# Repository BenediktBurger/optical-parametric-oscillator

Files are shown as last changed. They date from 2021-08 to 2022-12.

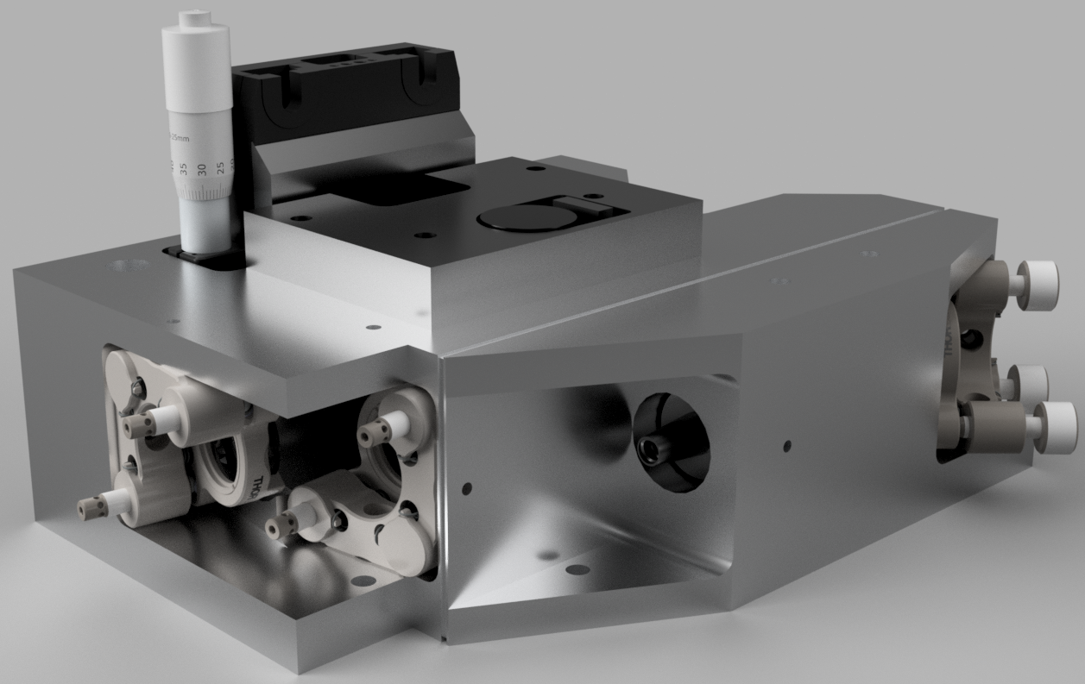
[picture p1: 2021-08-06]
images/CavityBlockSeitlich.png

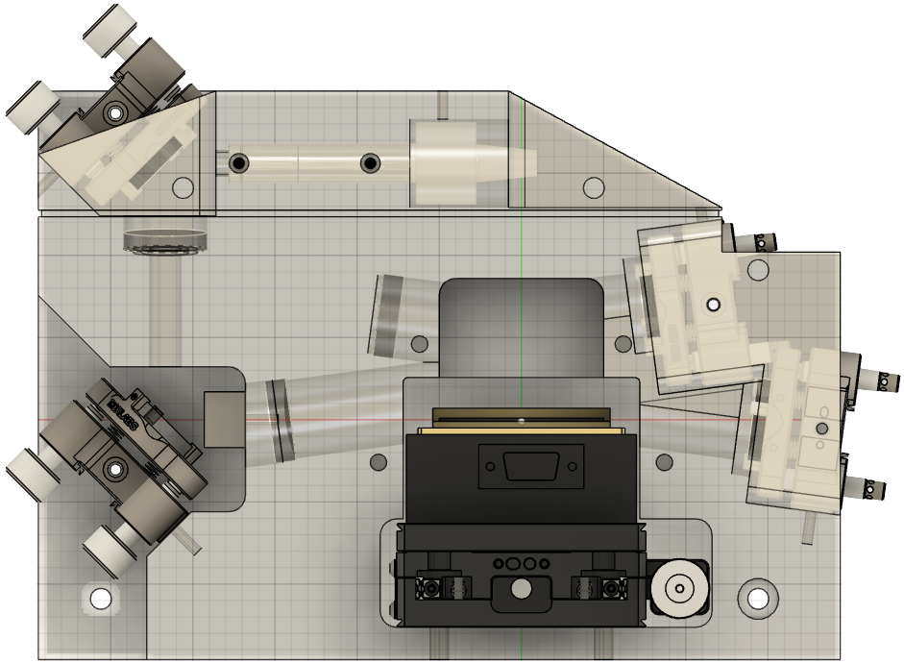
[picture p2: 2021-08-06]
drawings/OPO-Block-Oben2.png

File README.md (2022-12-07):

# Optical Parametric Oscillator

Open source hardware for a continuous wave optical parametric oscillator (OPO) in the mid-infrared regime.



## History

We needed a narrowband, tunable, continuous wave light source for coherent radiation at 606 nm. The result is this optical parametric oscillator with intra-cavity sum frequency generation, similar to a special version of the Aculight Argos 2400 laser system previously sold by Lockheed Martin. This is described in *Tunable, continuous-wave optical parametric oscillator with more than 1W output power in the orange visible spectrum* by S. Mieth et al. [DOI10.1364/OE.22.011182](https://www.osapublishing.org/oe/abstract.cfm?uri=oe-22-9-11182).

The design works for mid-infrared laser light as well, if the sum frequency part is left out. In fact, we use a second model with different mirror coatings and crystal for light at 2550 nm.

## Design Overview

The optical parametric oscillator consists in a bow-tie cavity (two concave mirrors with curvature radius of 100 mm and two planar mirrors) and a periodically poled lithium niobate crystal.

A pump laser at 1064 nm, focused into the center of the crystal, provides power for the difference frequency generation. The cavity is resonant (by mirror design) for one frequency (the *signal*) such that this frequency is amplified and the difference frequency (*idler*) is generated and emitted (see *singly resonant optical parametric oscillator*).

An etalon in the cavity (in the second focus) allows longitudinal mode selection for the signal wave.

## Folder Contents

- *designs* contains 3D designs.
- *drawings* contains some corresponding technical drawings.
- *images* contains some images and schematics of the design.
- *documentation* contains documentation of the setup.

## Construction

-The pump laser is a fiber laser by *IPG Photonics* (YAR-15K) with up to 15 W at 1064 nm. Its fiber tip contains a collimation unit (called *collimator*) with an additional clamp (made by Aculight) in order to mount it repeatedly with the same polarisation.
- Two highly reflective mirrors (1 inch diameter), mounted in *Thorlabs Polaris K1F* allow the pump beam to be adjusted.
- This collimator is mounted into the *OPO-Block* (see 3D file in *designs*) with a horizontal polarisation.
- A 0.5 inch lens with 62.9 mm focal length (*Newport KPX052AR.33*) focusses the pump power into the nonlinear crystal. It is mounted with the *Linsenhalter* (in designs).
- The nonlinear crystal is made of magnesium oxide doped (5%) lithium niobate with a periodic poling for *quasi phase matching*. A fanout structure of the poling period allows tuning via vertical translation. Use [SNLO](https://as-photonics.com/products/snlo/) for calculating the poling period. *HC Photonics* is capable of producing this crystal.
- The crystal is mounted in a heating oven (*HC Photonics TC038D*) for temperature controlling. For a python API controlling the oven temperature see [pymeasure](https://pymeasure.readthedocs.io).
- The oven is mounted to the OPO-Block via a translation stage (*Thorlabs XR25P_M*) and *Ofen-Adapterplatte* (in designs)
- Four specially coated 25mm mirrors (Anti-reflection for 1064 and the idler on both sides. Anti-reflection coating is for the signal on the outside and high-reflection on the inside), two mirrors with concave curvature of 100 mm (next to the oven) and two planar ones, form the cavity. Laseroptik made them in our case. Most important is the high reflectivity for the signal.
- One mirror is glued into the OPO-Block, one is mounted with a SM1 ring from Thorlabs and the other two (on the output side of the Block) are mounted with *Thorlabs Polaris K25F4_M* in order to adjust the cavity.
- Finally the Etalon is glued to a comercially available galvanometer (for Lasershows) and mounted to the lid *Deckel LwG* (in designs), which in turn is mounted on top of the OPO-Block to provide radiation blocking and reduce dust entering the cavity.
- For the setup and adjustments refer the files in *documentation*.

## Disclaimer

These files are provided by the copyright holders and contributors "as is" and any express or implied warranties, including, but not limited to, the implied warranties of merchantability and fitness for a particular purpose are disclaimened. In no event shall the copyright owner or contributors be liable for any direct, indicrect, insidental, special, exemplary, or consequential damages however caused and on any theory of liability, wheter in contract, strict liability, ort tort (including negligence or otherwise) arising in any way out of the use of these files, even if advised of the possibility of such damage.

This is a class IV laser system. Adhere to local regulations and apply necessary safetey measurements.

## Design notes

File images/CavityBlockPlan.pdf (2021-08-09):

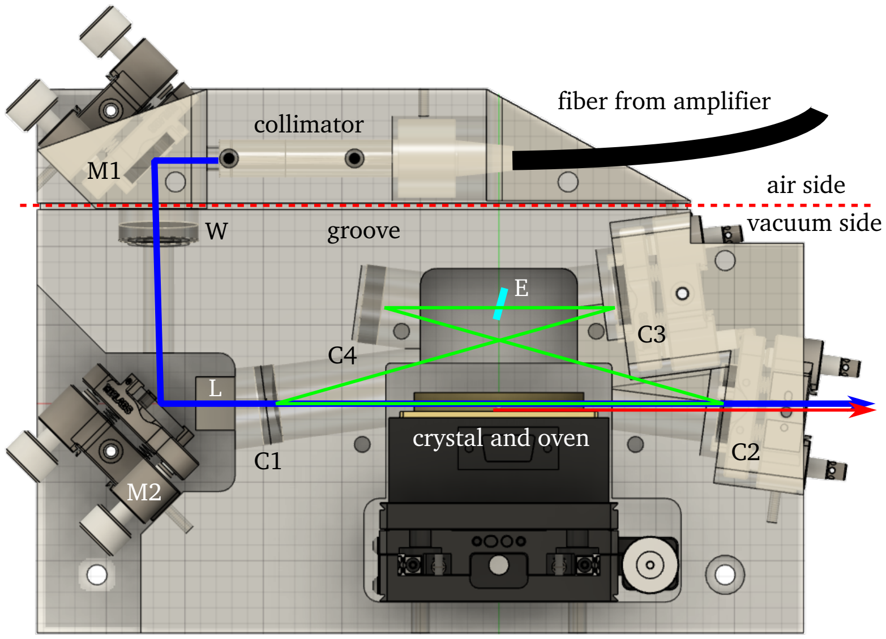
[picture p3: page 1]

collimator
M1

M2

W

L

C1 | C2

C3
C4

crystal and oven

groove

air side
vacuum side

E

fiber from amplifier

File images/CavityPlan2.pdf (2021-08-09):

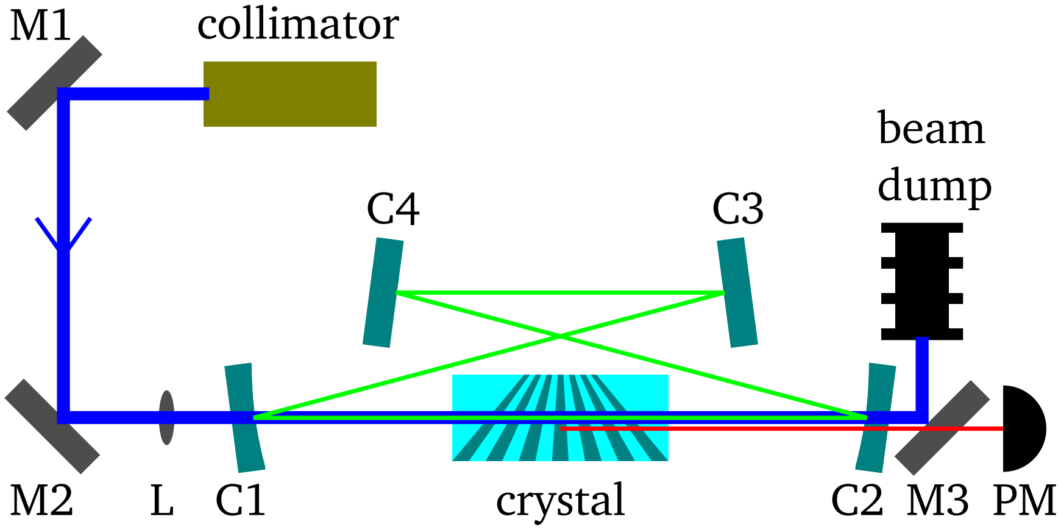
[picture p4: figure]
collimator; beam dump; crystal

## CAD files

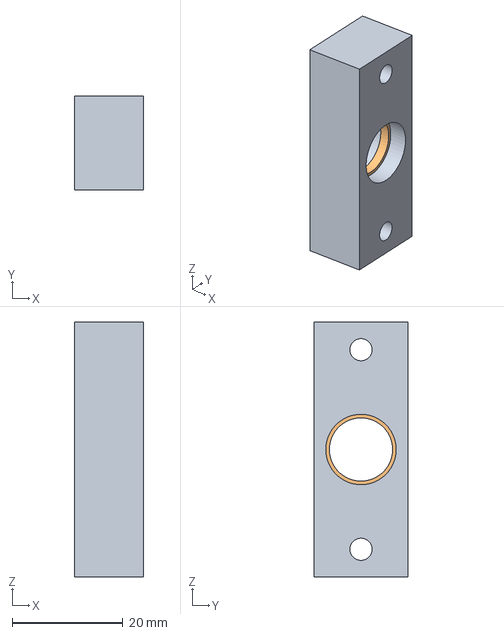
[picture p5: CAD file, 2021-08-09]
designs/Linsenhalter.step
12.5 x 17.0 x 46.0 mm

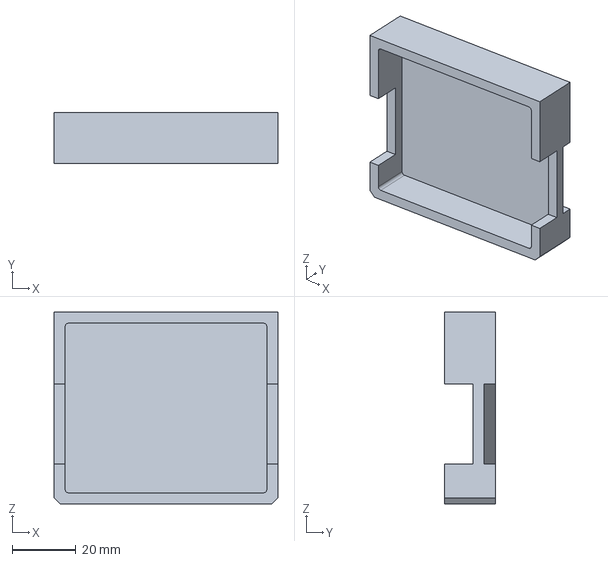
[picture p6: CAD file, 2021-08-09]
designs/Ofen-Deckel.step
70.0 x 16.0 x 60.0 mm

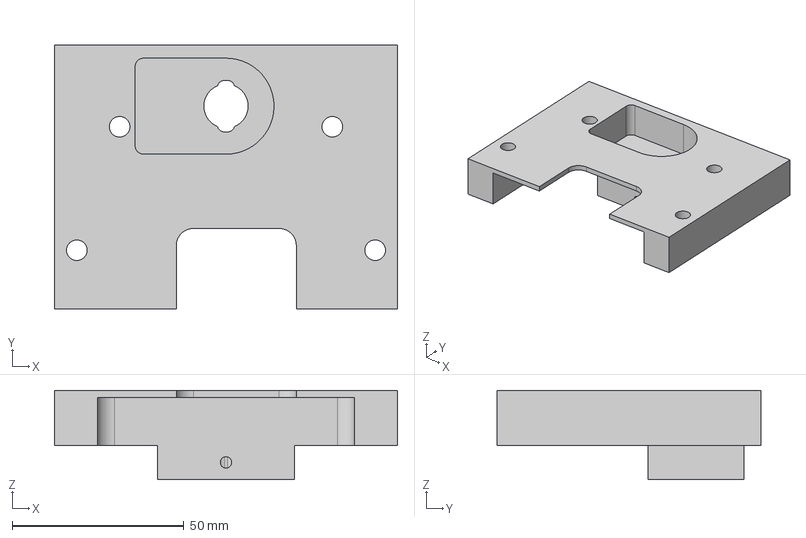
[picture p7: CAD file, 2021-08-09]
designs/Deckel LwG.step
100.0 x 77.0 x 26.0 mm

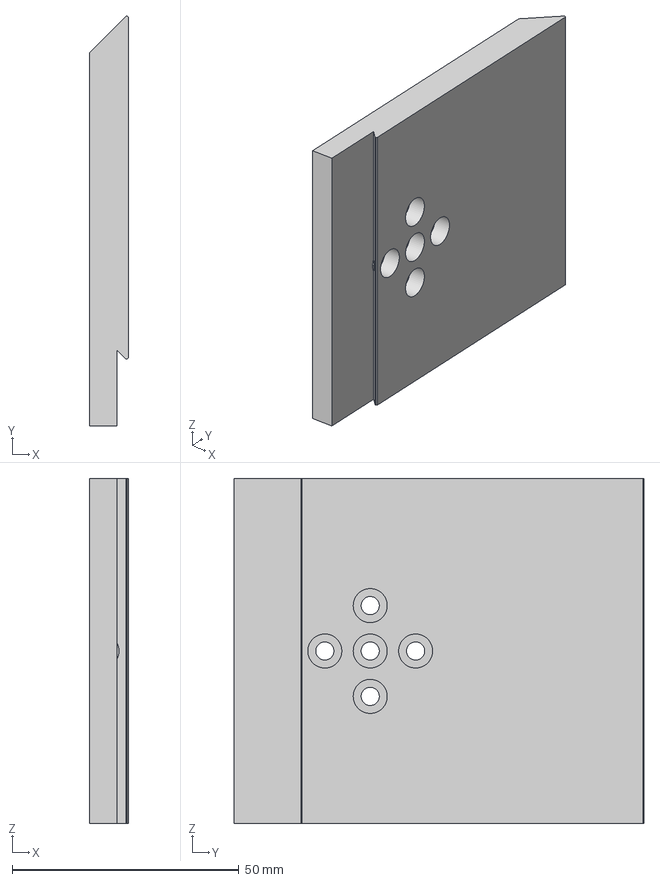
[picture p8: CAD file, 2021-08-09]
designs/Ofen-Adapterplatte.step
8.50 x 90.3 x 76.0 mm

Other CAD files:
designs/Deckel LwG.f3d
designs/OPO-Block.f3d
designs/Ofen-Adapterplatte.f3d

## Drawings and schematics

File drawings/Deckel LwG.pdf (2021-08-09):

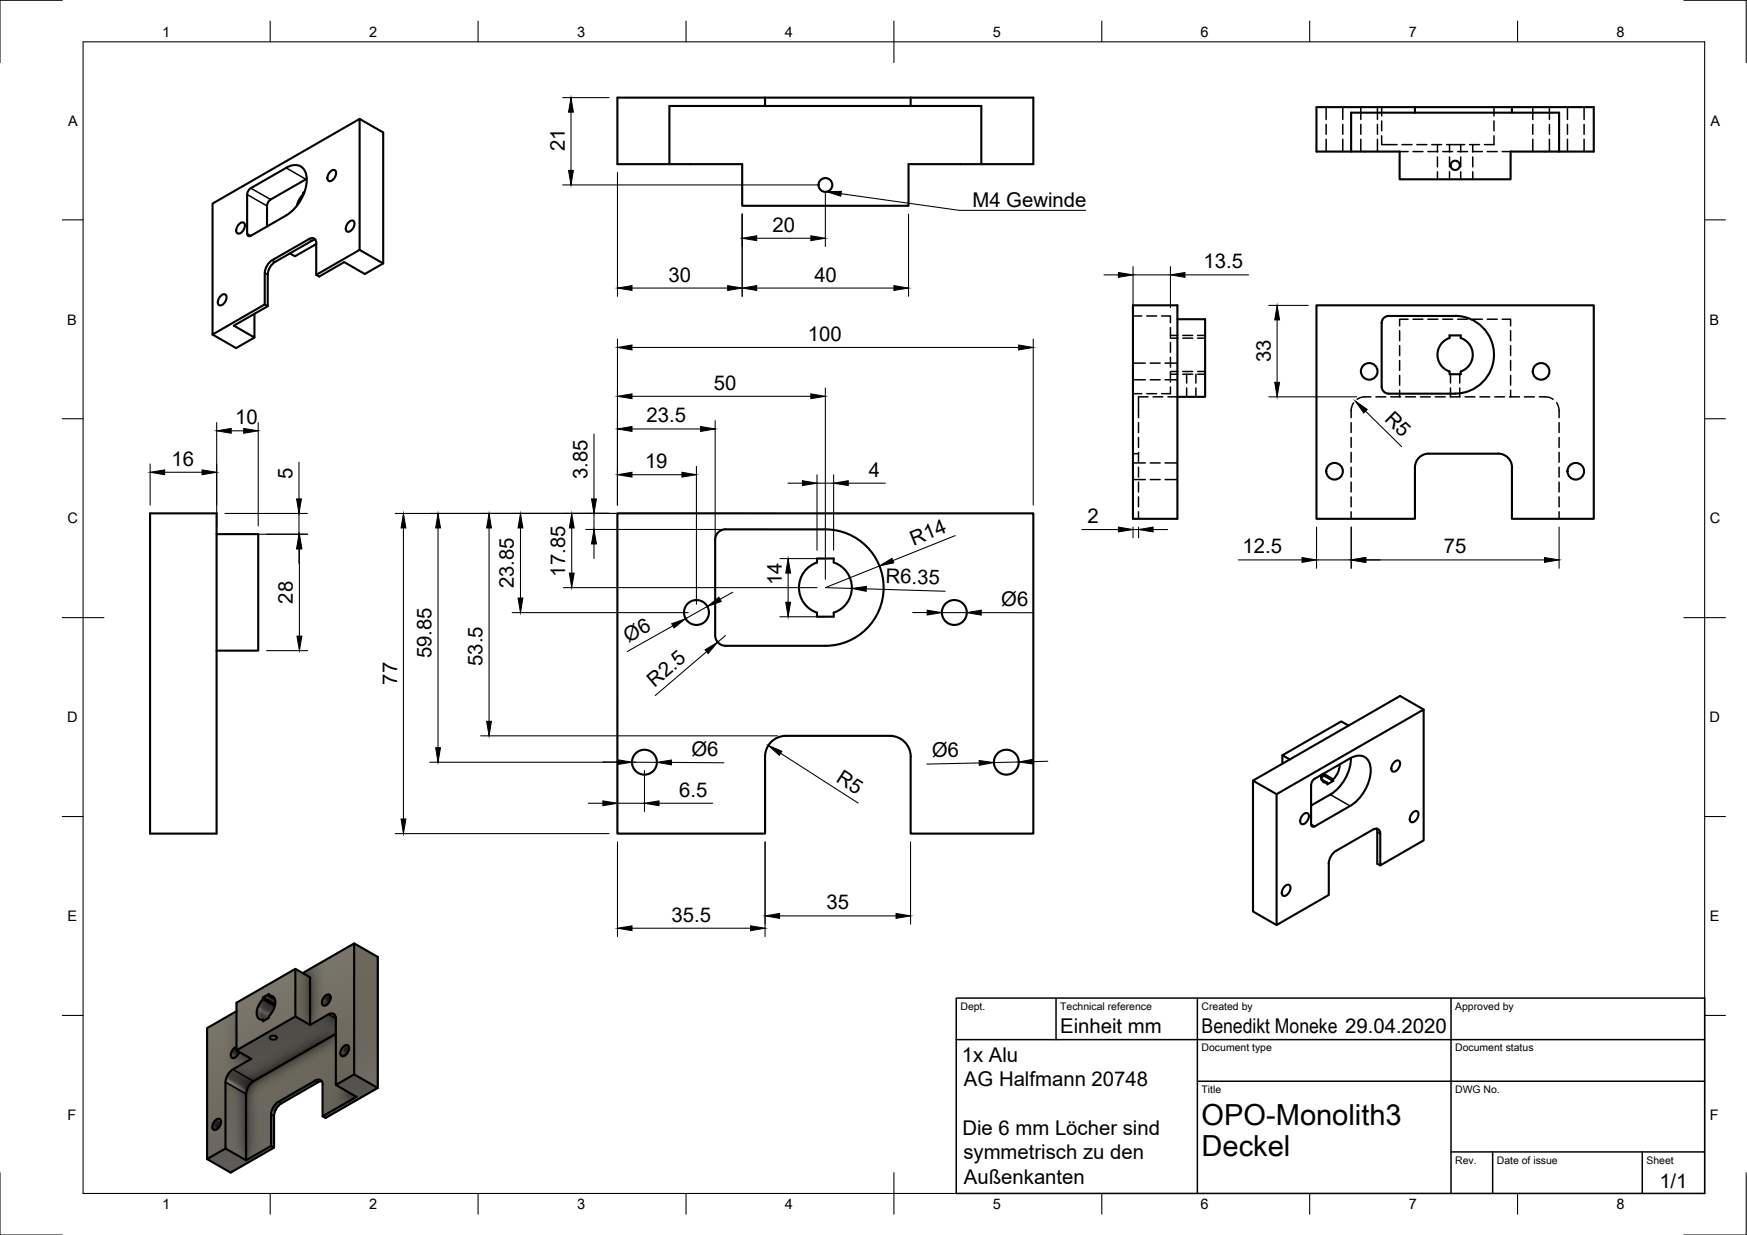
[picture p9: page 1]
M4 Gewinde 53.5

Dept. | Technical reference Einheit mm | Created by Benedikt Moneke 29.04.2020 | Approved by

1x Alu AG Halfmann 20748 Die 6 mm Löcher sind symmetrisch zu den Außenkanten | | Document type | Document status

Title OPO-Monolith3 Deckel | DWG No.

Rev. | Date of issue | Sheet 1/1

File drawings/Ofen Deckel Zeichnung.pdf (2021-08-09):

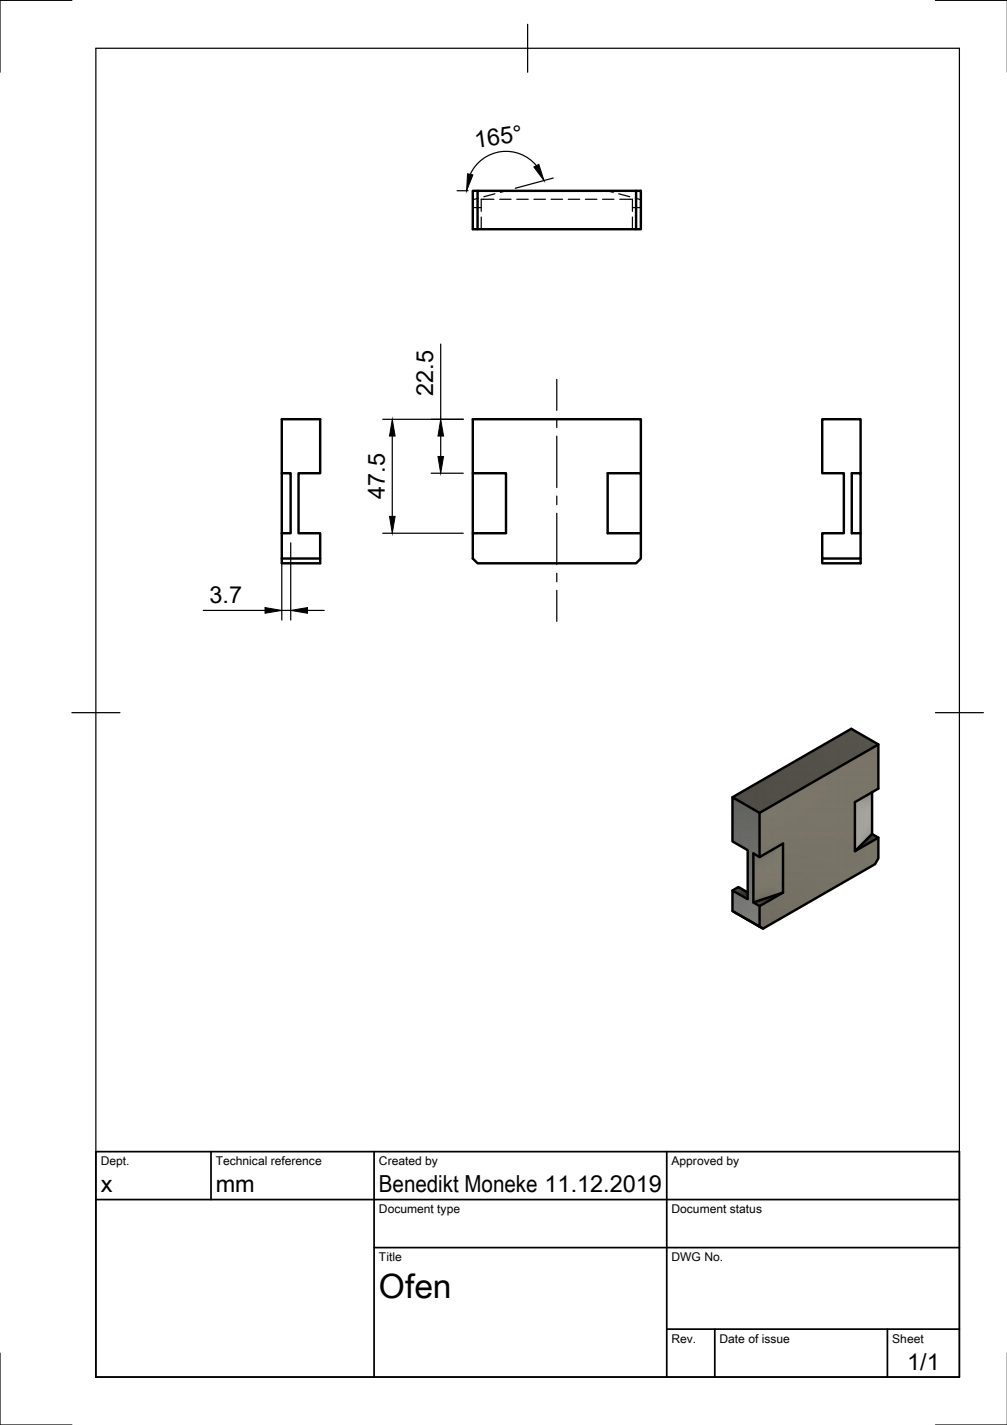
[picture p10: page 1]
Benedikt Moneke 22.5 47.5

Dept. | Technical reference | Created by 11.12.2019 | Approved by

Document type | Document status

Title Ofen | DWG No.

Rev. | Date of issue | Sheet 1/1

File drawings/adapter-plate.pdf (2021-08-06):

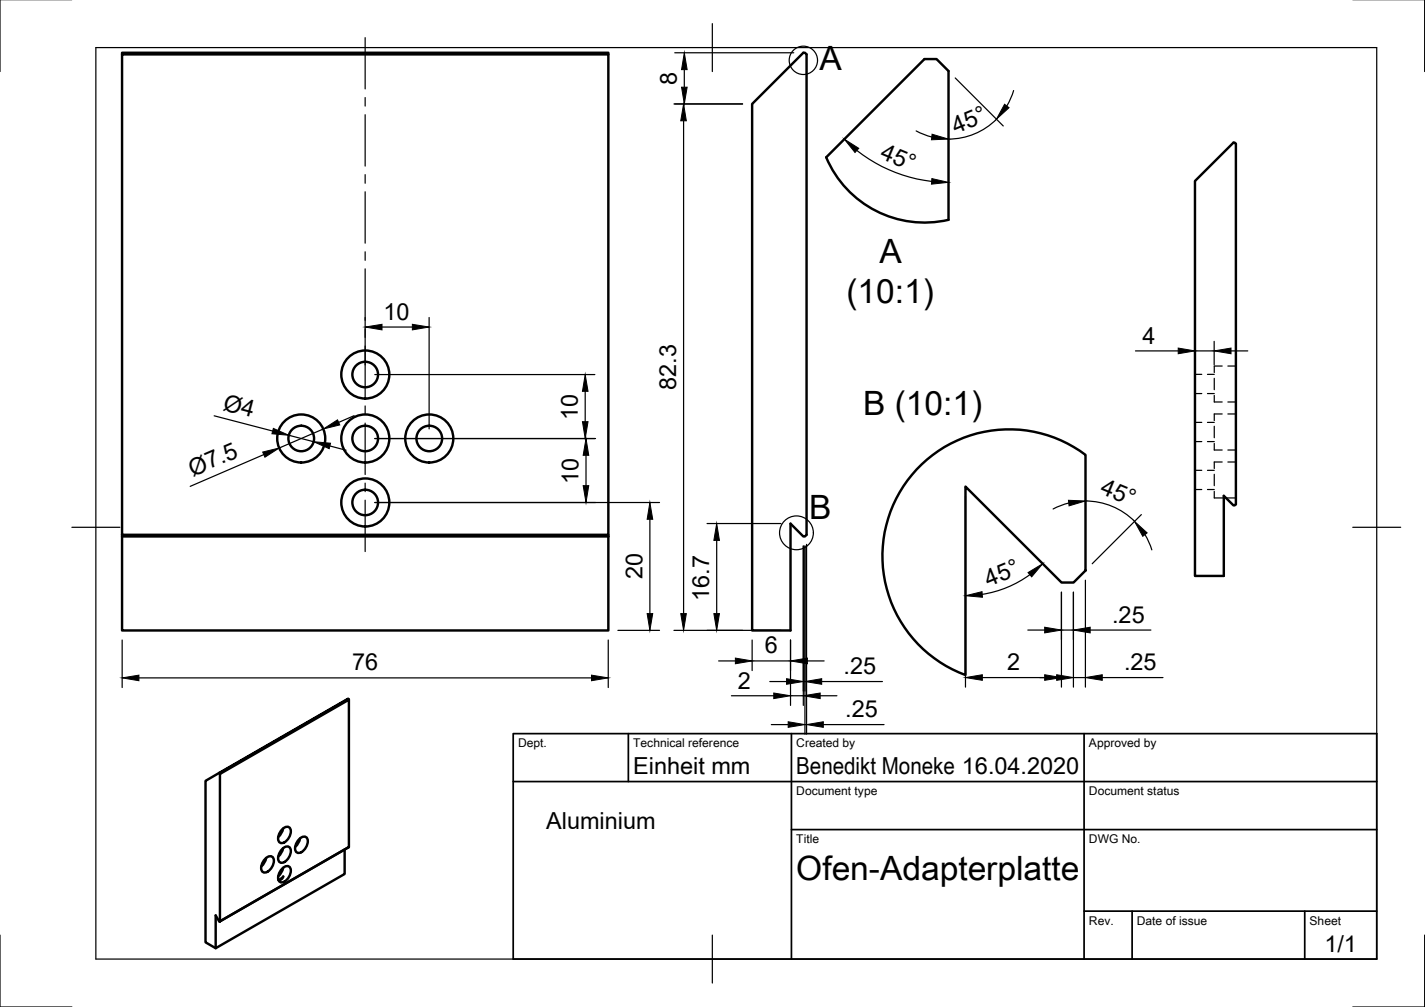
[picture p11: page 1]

Dept. | Technical reference Einheit mm | Created by Benedikt Moneke 16.04.2020 | Approved by

Aluminium | | Document type | Document status

Title Ofen-Adapterplatte | DWG No.

Rev. | Date of issue | Sheet 1/1

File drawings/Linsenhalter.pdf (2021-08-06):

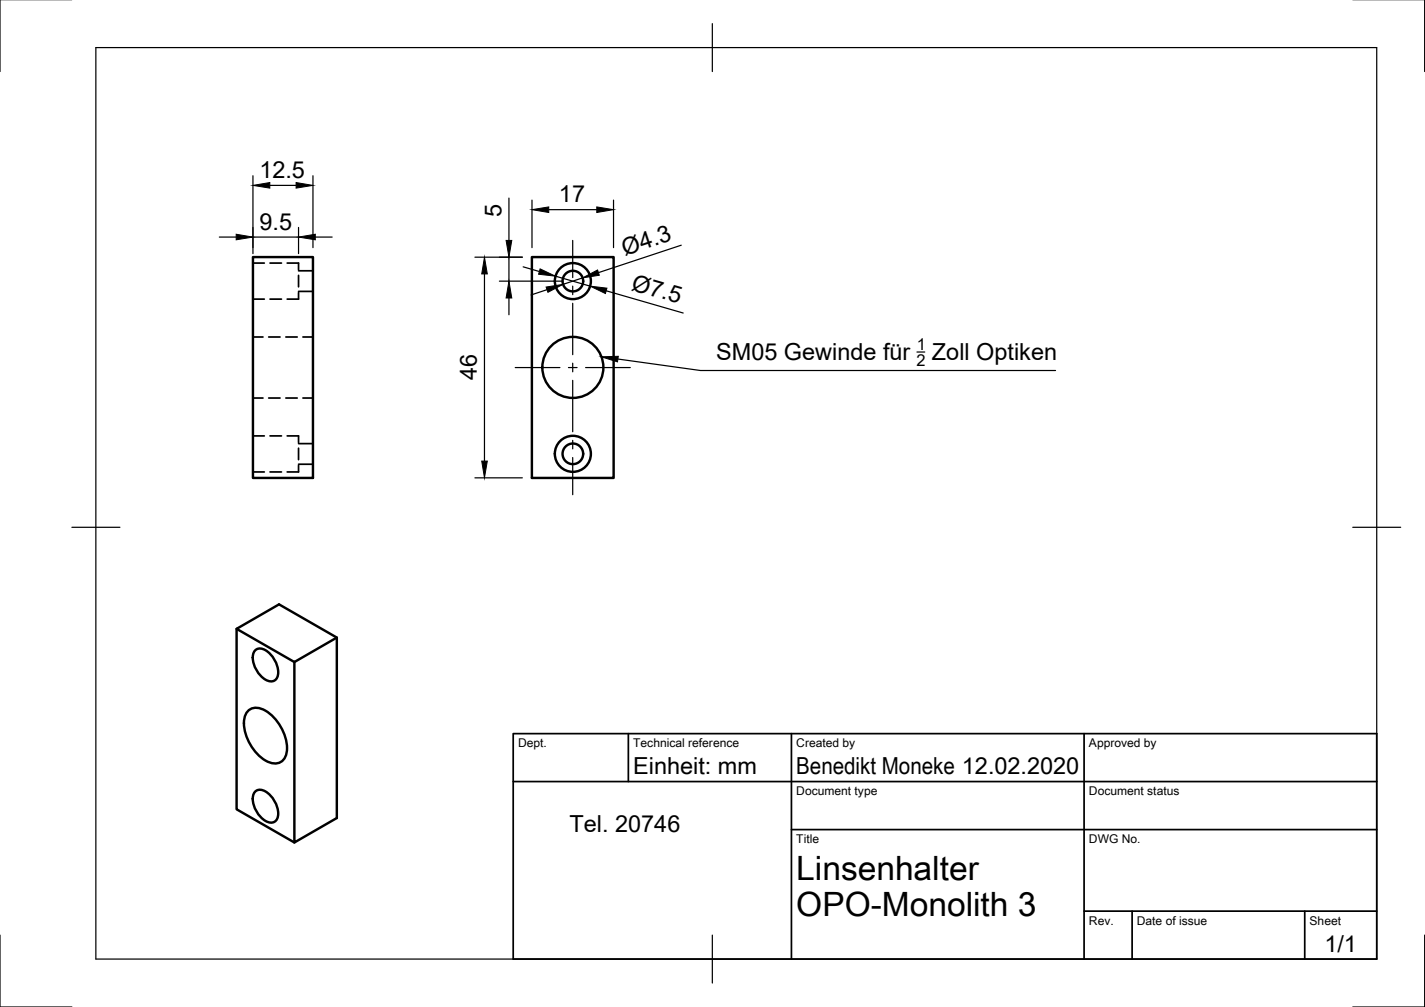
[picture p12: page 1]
SM05 Gewinde für 1; Zoll Optiken

Dept. | Technical reference Einheit: mm | Created by Benedikt Moneke 12.02.2020 | Approved by

Tel. 20746 | | Document type | Document status

Title Linsenhalter OPO-Monolith 3 | DWG No.

Rev. | Date of issue | Sheet 1/1

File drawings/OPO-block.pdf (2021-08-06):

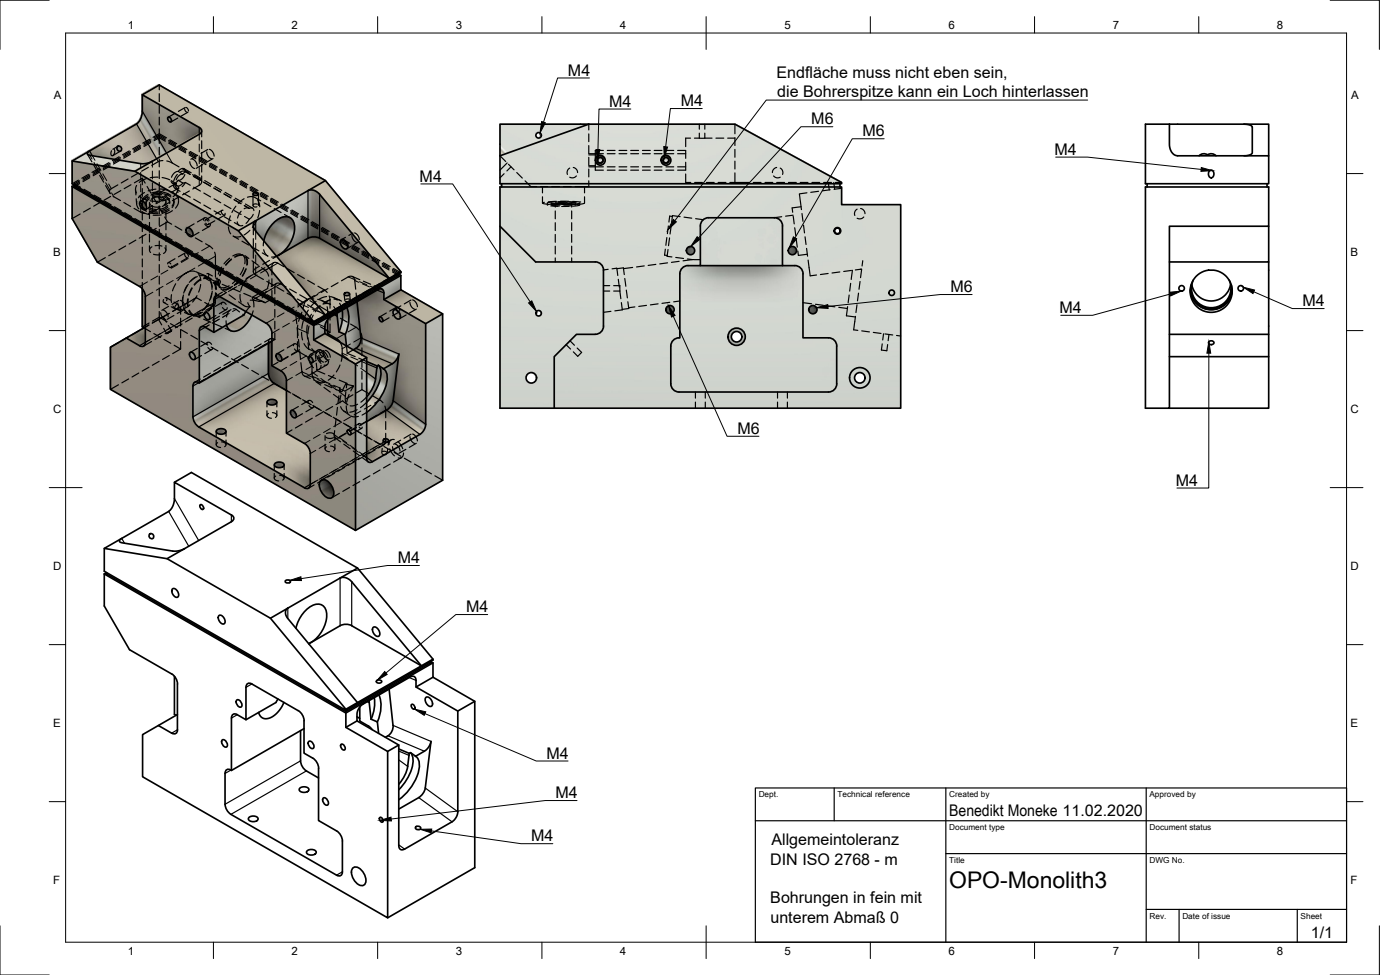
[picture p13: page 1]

Endfläche muss nicht eben sein,
die Bohrerspitze kann ein Loch hinterlassen

Dept. | Technical reference | Created by Benedikt Moneke 11.02.2020 | Approved by

Allgemeintoleranz DIN ISO 2768 - m Bohrungen in fein mit unterem Abmaß 0 | | Document type | Document status

Title OPO-Monolith3 | DWG No.

Rev. | Date of issue | Sheet 1/1

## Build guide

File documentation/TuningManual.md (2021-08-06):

# Anleitung zur Justage eines OPOs

Die Informationen dieser Anleitung wurden aus der Justage des OPOs für [Experiment] META Aufbau neuer OPO und bei [Experiment] META MOT606 Conversion von 795 nm zu 606 nm gewonnen und nutzen die Tipps, die von verschiedenen Anwendern des Moduls Aculight Argus von Lockheed Martin gegeben wurden.

## Anwendungsbereich

Das Wissen wurde an OPOs gewonnen, die infrarot (1064 nm) gepumpt werden und deren Signalstrahlung (kürzere Wellenlänge der Differenzfrequenzgeneration) in einem Resonator um den periodisch gepolten nichtlinearen Kristall (PPLN) umläuft. Der Resonator ist in Doppel-Z-Konfiguration aufgebaut. Die Spiegel direkt am Kristall sind gekrümmt, die anderen planar.

Für die weiteren Hinweise gilt folgende Nomenklatur:

- *Einkoppler* ist der gekrümmte Kavitäts-Spiegel, durch den die Pumpe in die Kavität eingekoppelt wird.
- *Auskoppler* ist der gekrümmte Kavitäts-Spiegel, durch den Pumpe, Idler und sichtbares Licht ausgekoppelt wird.
- *Gegeneinkoppler* ist der planare Kavitäts-Spiegel, der gegenüber dem Einkoppler und zu diesem parallel steht.
- *Gegenauskoppler* ist der planare Kavitäts-Spiegel, der gegenüber dem Auskoppler und zu diesem parallel steht.

## 1. Aufbau und Vorjustage

Zu Beginn müssen die Spiegel an ihren Plätzen und in richtiger Ausrichtung aufgebaut werden, wozu eine Papierskizze helfen kann. Zur genaueren Ausrichtung kann ein sichtbarer Laserstrahl, zum Beispiel ein roter Diodenlaser oder ein grüner Laserpointer verwendet werden, solange das Licht einen Umlauf im Resonator machen kann. Dieser temporäre Laserstrahl sollte zwei Spiegel zentral treffen und die Spiegel so justiert werden, dass der Strahl einmal umläuft. Dazu ist es hilfreich, wenn der Kristall noch nicht verbaut ist. Auch kann man die Strahlen erst anhand der angefertigten Skizze ausrichten.

Der Kristall ist so verbaut, dass eine Höhenänderung die Polungsperiode ändert und er nur 0,5-1 mm breit ist.

Zur leichteren Justage sollte kein Etalon im Resonator eingebaut sein.

## 2. Justage der Pumpe

Die Pumpe sollte anfangs, mit schwacher Leistung, zentral auf die beiden gegenüberliegenden Spiegel (Einkoppler, Auskoppler) ausgerichtet werden, anschließend der Kristall eingebaut und die Pumpe so horizontal justiert werden, dass sie vorne zentral den Kristall trifft und hinten zentral verlässt, dazu ist eine Strahlkamera hilfreich, oder mit einer Wandlerkarte. Dadurch ist der Strahl in der horizontalen durch Ort und Winkel justiert.

In den verwendeten Kristallen enstand ab 0,5 W Pumpleistung die Frequenzverdoppelte der Pumpleistung, diese Frequenzverdoppelte (bei 532 nm, ab jetzt grünes Licht genannt) ist hilfreich zur weiteren Justage.

Der vertikale Ort ist relativ unwichtig, da er duch die Kristallverschiebung eingestellt wird. Der Winkel ist wichtig, um möglichst eine konstante Polungsperiode für die Pumpe zu haben. Der Winkel wird über den Spiegel der Pumpstrahlung eingestellt, der am nächsten der Kavität steht. Die verwendeten Kristalle hatten eine Beschichtung, die einen signifikanten Anteil grünen Lichtes reflektiert, sodass der Kristall wie ein Etalon wirkt und bei vertikaler Verkippung eine vertikale Reihe von Punkten erzeugt. Ziel ist es, diese Punkte zu überlagern, um ungefähr senkrecht auf den Kristall zu treffen. Umso näher man diesem Punkt kommt, umso heller wird das grüne Licht und der senkrechte Treffer zeigt sich durch eine markante Intensitätsspitze. Zwischen dem Ort maximaler Intensität und dem Ort bester Überlagerung liegt der Ort, der später die höchste Leistung bringt. Am besten auf maximale Intensität einstellen und leicht in Richtung einen Punkt gehen. Es empfiehlt sich diese vertikalen Punkte auf einem reflektierten Strahl anzuschauen, an dem die Pumpe nicht mehr vorhanden ist. Eine sinnvolle Einstellung sind 1-3 W, um genug grünes Licht zu haben.

Mit senkrechtem Treffer auf die Kristalloberfläche und guter Strahlführung durch den Kristall ist die Pumpe fertig justiert, sofern die Kavität justierbar ist.

## 3. Grobjustage der Kavität

Es empfiehlt sich, die Spiegel, die von der Pumpe durchlaufen werden (zumindest den Einkoppler), nicht anzufassen, um die Pumpe während der Justage nicht abzulenken und den Kristall zu beschädigen. Justiert wird mit Hilfe der anderen Spiegel.

Auch hier wird grünes Licht verwendet, aber nur das Licht, das vorne aus dem Kristall austritt und nicht dasjenige, das an der Austrittsseite reflektiert wird und rückwärtig umläuft. Man beobachtet das grüne Licht, das aus einem oder mehreren Spiegeln austritt an verschiedenen Orten: Nahe am Spiegel und weiter entfernt, ca 15-30 cm. Nun versucht man das Licht, das direkt aus dem Spiegel austritt mit demjenigen zu überlagern, das nach einem weiteren Umlauf erst austritt. Mit einem ersten Spiegel (Auskoppler oder Gegenauskoppler) wird auf den nahen Ort justiert, mit einem späteren Spiegel (zum Beispiel Gegeneinkoppler) wird auf den fernen Ort justiert.

Um zu erkennen, welches Licht einen weiteren Umlauf hinter sich hat, muss man den Resonator an einem Ort blocken, wo nur Licht lang kommt, das mindestens einen vollen Umlauf hat, aber keines, das auf den Schirm fällt.

Um den ersten Umlauf durch den Kristall zu justieren, kann man mit dem ersten Spiegel auf den Eintritt des Kristalls justieren und mit dem zweiten auf den Austritt. Wenn man eine feste Montage hat, zum Beispiel einen OPO Block, kann man leichter den Strahl zwischen den planaren Spiegeln parallel zum OPO-Block mit Hilfe des ersten Spiegels justieren. Anschließend justiert man mit dem zweiten Spiegel auf die Eintrittsfläche des Kristalls. Durch die Geometrie des Blocks sollte der Strahl gerade durch den Kristall gehen und man kann die Strahlen überlagern.

Bei einer guten Überlagerung bilden die Ränder der beiden Punkte ein Interferenzmuster, das wie Schmodder aussieht. Berührt man jedoch die Justierschrauben leicht, so ändert sich dieses Muster stark und ist somit als Interferenzmuster erkennbar.

Je nach Beschichtung der Spiegel, reflektiert auch die Rückseite der Spiegel das grüne Licht und man erhält eine horizontale Reihe von Punkten. In diesem Fall überlagert man den jeweils die hellsten Punkte der verschiedenen Reihen.

## 4. Feinjustage der Kavität

Wenn man den vorherigen Schritt gut gemacht hat, sollte der OPO-Prozess bei genügend Pumpleistung anlaufen. Möglicherweise muss man den Kristall ein wenig in seiner Position variieren oder an einem der Spiegel leicht drehen, um den Prozess zu starten. Mit einem Leistungsmessgerät, das die Leistung des Idlers misst, nachdem man die Pumpe rausgefiltert hat, kann man die Kavität auf maximale Leistung des Idlers justieren. Auch hier reicht es die zwei planaren Spiegel zu benutzen. Es empfiehlt sich bei stabiler OPO-Leistung die Pumpe (vertikaler Winkel) auf Leistung nachzujustieren und danach die Kavität weiterzujustieren.

Die Idler sind meist mittelinfrarot, also bieten sich thermische Messköpfe an. Auf ausreichende Leistungsreserven achten, die von uns verwendeten OPOs haben Ausgangsleistungen von ca 1 W.
